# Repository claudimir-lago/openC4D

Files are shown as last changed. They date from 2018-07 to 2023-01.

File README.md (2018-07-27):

# openC4D
#### _A Capacitively Coupled Contactless Conductivity Detector (C4D) for Capillary Electrophoresis._

To the best of our knowledge, this is still the smallest Capacitively Coupled Contactless Conductivity Detector (C4D) … and it’s open!

Our first C4D was introduced in 1998 [1], and after trials and errors, we published an improved version in 2009 [2]. Here, the continuously improved version is available.

What is here?

•	The plans to build __the printed circuit boards for the detector__ itself. It must be powered, and the signal is available as a digital output in a serial format.

•	__The microcontroller board.__ Although the detector module can be used in a dedicated instrument, this board allows one to control up to four C4Ds through a USB port.

•	__The firmware.__ An Arduino firmware to be used in the microcontroller board.

•	__The frontend.__ A Java frontend to be used to get electropherograms.

We have some papers if you wish to learn more about our CE-C4D [1-8].

1.	da Silva, J.A.F. and C.L. do Lago, An oscillometric detector for capillary electrophoresis. Analytical Chemistry, 1998. 70(20): p. 4339-4343.
2.	Francisco, K.J.M. and C.L. do Lago, A compact and high-resolution version of a capacitively coupled contactless conductivity detector. Electrophoresis, 2009. 30(19): p. 3458-3464.
3.	Brito-Neto, J.G.A., et al., Understanding capacitively coupled contactless conductivity detection in capillary and microchip electrophoresis. Part 1. Fundamentals. Electroanalysis, 2005. 17(13): p. 1198-1206.
4.	Brito-Neto, J.G.A., et al., Understanding capacitively coupled contactless conductivity detection in capillary and microchip electrophoresis. Part 2. Peak shape, stray capacitance, noise, and actual electronics. Electroanalysis, 2005. 17(13): p. 1207-1214.
5.	Francisco, K.J.M. and C.L. do Lago, A capillary electrophoresis system with dual capacitively coupled contactless conductivity detection and electrospray ionization tandem mass spectrometry. Electrophoresis, 2016. 37(12): p. 1718-1724.
6.	Francisco, K.J.M. and C.L. do Lago, Improving thermal control of capillary electrophoresis with mass spectrometry and capacitively coupled contactless conductivity detection by using 3D printed cartridges. Talanta, 2018. 185: p. 37-41.
7.	Saito, R.M., et al., Ionic mobility of the solvated proton and acid-base titration in a four-compartment capillary electrophoresis system. Analytical Methods, 2010. 2(2): p. 164-170.
8.	da Silva, J.A.F., N. Guzman, and C.L. do Lago, Contactless conductivity detection for capillary electrophoresis - Hardware improvements and optimization of the input-signal amplitude and frequency. Journal of Chromatography A, 2002. 942(1-2): p. 249-258.

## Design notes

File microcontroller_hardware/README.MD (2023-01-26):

This microcontroller board allows you to connect up to four openC4Ds to an USB port. Then, you can use the [frontend](https://github.com/claudimir-lago/openC4D/tree/master/frontend) for data acquisition or send [Serine commands](https://github.com/claudimir-lago/openC4D/blob/master/firmware/Manual_openC4D_3.pdf) using a [terminal program](https://sites.google.com/site/terminalbpp/).

The original version of the board is based on a [Teensy 2.0 board](https://www.pjrc.com/store/teensy.html), and the one-layer PCB was created in [Eagle](https://www.autodesk.com/products/eagle/free-download). Unfortunately, Teensy 2.0 was discontinued. So, for new projects, consider the Arduino-shield version.

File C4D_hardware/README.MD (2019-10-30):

# Building an openC4D
### _The basics about what you have here_

The openC4D is composed of four printed circuit boards (PCBs): the oscillator, the rectifier, and two shielding boards. Inside the folders Oscillator and Rectifier, you will find the schematics and PCB images. The original files were made in [DipTrace](https://diptrace.com/download/download-diptrace/).

Whether you wish a fast track, go straight to Gerber and send the files to some place for the production of a panel with PCBs for one complete openC4D.

### _An warning about the previous version of the printed circuit boards_

The previous version of the PCBs was made available as a panel with the boards for three detectors. There was, however, a small but important failure in the tracks. Unfortunately, two tracks were merged in some point during the production, and now they must be fixed. Figure 1 shows that board and the two small cuts that must be done in the oscillator board. You can use a sharp (and hard) device to cut the merged tracks… and that’s all.

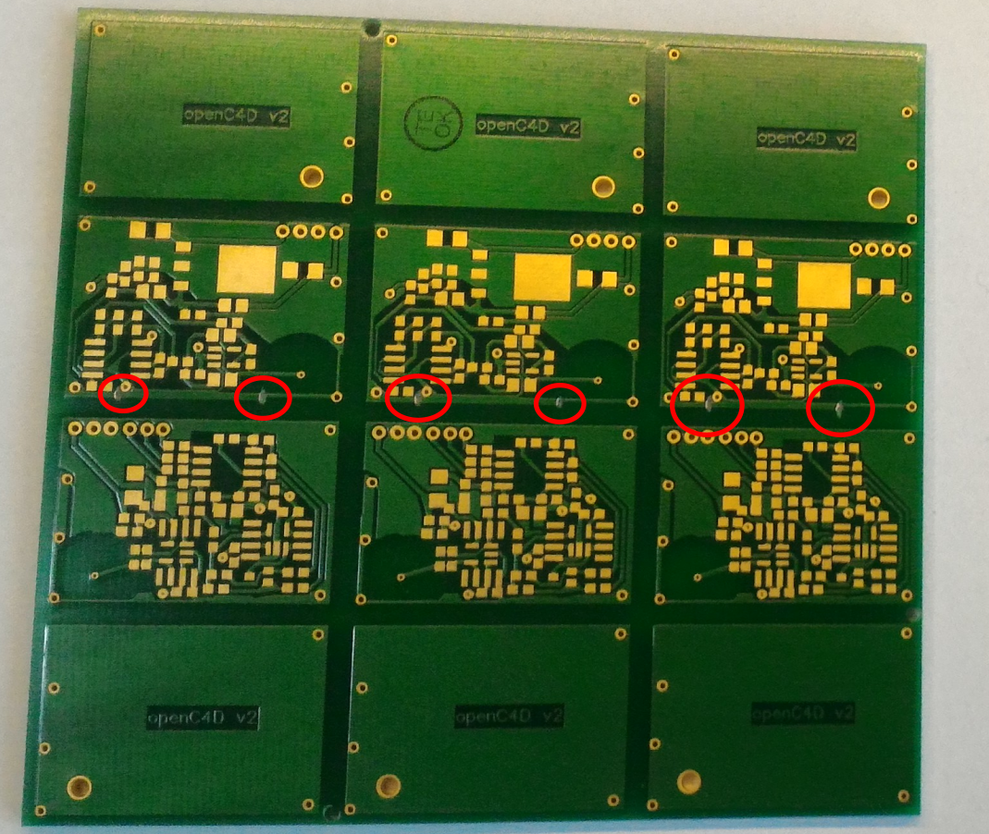
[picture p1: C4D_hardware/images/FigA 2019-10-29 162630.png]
Figure A

#### _Figure 1._ The red circles show where to cut the tracks. Don’t worry, because there are redundant tracks keeping the right connections between the parts.

### _A step-by-step building process (with tips and tricks)_

Although the present files are for one detector, this tutorial is based on the previous paneled version, but don’t worry. As shown in Figure 2, after marking the borders and cutting off the boards, you will have essentially the same boards that you need to build the openC4D.

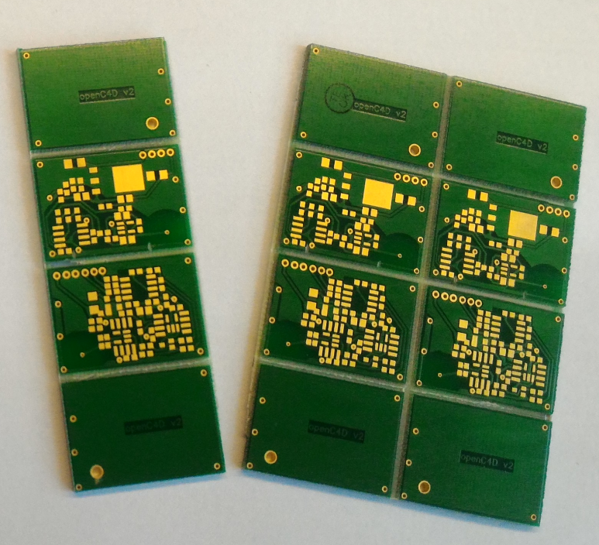
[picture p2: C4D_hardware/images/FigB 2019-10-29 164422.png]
Figure B

#### _Figure 2._ We used a CNC machine to make the grooves between all PCBs, but you can use any other method to cut FR04 PCBs. After that, the PCBs are separated, and the borders are sanded accordingly.

The four PCBs will be assembled as a “sandwich”, but we need the stuffing for the sandwich: two insulant layers and the ground plane, as shown in Figure 3. These layers will be put between the oscillator and rectifier PCBs and will determine the gap between the electrodes, which essentially determine the detection length.

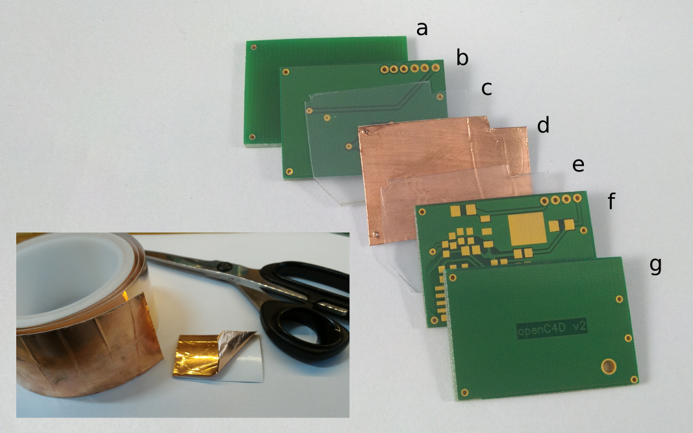
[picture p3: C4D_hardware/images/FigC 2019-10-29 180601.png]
Figure C

#### _Figure 3._ The set of seven layers of an openC4D: shield PCBs (a and g), rectifier PCB (b), insulating layers (c and e), copper ground plane (d), and oscillator PCB (f). The copper layer was prepared from a copper foil tape (shown in the inset). After cutting, the copper layer is pulled off and stick to one of the insulating layers.

Different materials can be used for the insulating and ground plane layers.

In Figure 3, the material used to make the insulating layers was a 0.25-mm PVC foil – actually, it was previously part of the cover of an old notebook. Obviously, the companies create the cover to cover a document and not necessarily to be used as an insulating layer. We’ve learned that some black covers are not appropriate, because they become somewhat conductive at high frequency (must likely because of the black filler or pigment).

The ground plane can be made of aluminum, copper, brass, or other conductive material. Copper foil tape is convenient, because it is thin and self-adhesive. Thicker foils will increase the coupling of the ground plane with the solution inside the capillary, and it is not good. At the same time, the thin foil of copper can be stick to one of the insulation layer, which ease the alignment of the different layers.

Be careful in making the holes through which the capillary will pass. For instance, a small barb in the copper layer could get into electrical contact with one of the electrodes from either the oscillator or the rectifier PCBs. Make sure, thus, that the holes are clear of barbs to prevent short circuits. 

The PCBs were prepared for SMD components, but there are a two options for the integrated circuits (ICs) U1 and U2 in the rectifier PCB: 5-pin SOT-23 and 8-pin SOIC. Figure 4 shows PCBs populated with these two kinds of components. SOT-23 has a smaller footprint, but SOIC is more popular. The idea was to make a board that could accept these two different versions of operational amplifiers available in the market. There is, however, a very important trick here: **the 5-pin SOT-23 must be soldered upside-down!!!** This was the price to make the board flexible and simple at the same time. Whether you can get the 8-pin SOIC version, buy it because it is safer and usually cheaper solution.

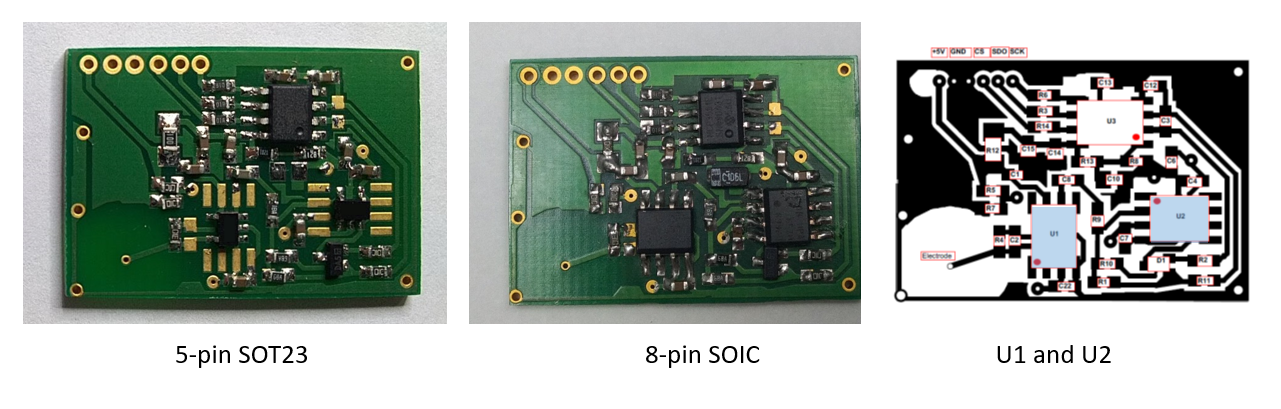
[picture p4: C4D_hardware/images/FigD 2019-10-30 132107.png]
Figure D

#### _Figure 4._ The rectifier PCB populated with the two versions of U1 and U2. It sounds strange, but the 5-pin SOT-23 ICs must be positioned upside-down before soldering.

Although a connector can be soldered at the border of the PCB, we’ve used to solder the cable to the boards, because the final setup is more robust and compact. In this case, make sure that the solder joint has a low profile as shown in Figure 5 in order to prevent that it touches the other PCB. You should try to make a proper [solder joint]( https://learn.adafruit.com/adafruit-guide-excellent-soldering/tools) and cut off the excess after that.

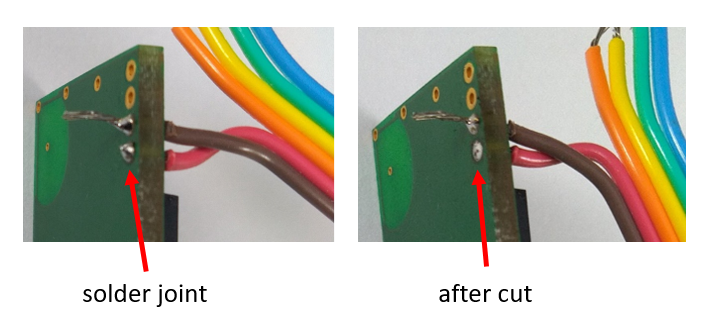
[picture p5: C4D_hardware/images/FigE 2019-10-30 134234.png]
Figure E

#### _Figure 5._ Pictures of a solder joint before and after the cutoff.

Before finishing, it is a good idea to check the voltages and waveforms at the test points.

The wave at the output of U1.2 (Figure 6) should be a square wave swinging between 0 and 5 V at a frequency around 1 MHz. A triangular wave is expected at the output of U1.1 and its amplitude should be about 4 V. At the output of U2 a sine wave is expected with amplitude also of 4 V. Although the original values of the resistors and capacitors were calculated according to these directives, the experimental result is not always the same. Sometimes only minor nonconformities are detected. However, sometimes the result is quite different. Unfortunately, there is no other way but changing resistors and capacitors. It is possible to calculated the values, but it is important having in mind some hints:

•	The higher either R2 or C1, the lower the oscillation frequency;

•	R1/R3 determines the amplitude of the triangular wave;

•	U2.1 with R4, R5, R6, C6, and C7 are a [multiple feedback low-pass filter](http://sim.okawa-denshi.jp/en/OPtazyuLowkeisan.htm) that should cut off the harmonics of the triangular wave and give a small gain to the fundamental frequency.

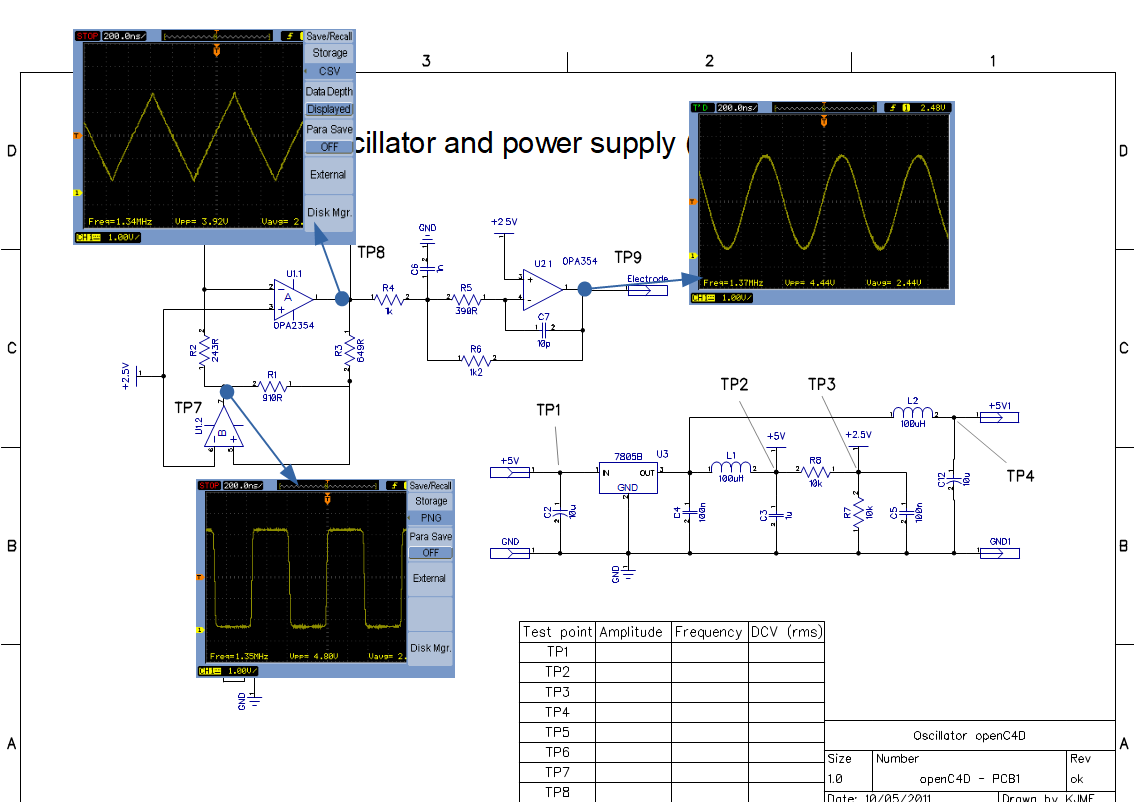
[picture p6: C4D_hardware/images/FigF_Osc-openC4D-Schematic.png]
Figure F

#### _Figure 6._ Waveforms at the most important test points in the oscillator board.

The waveform at the output of the transimpedance amplifier (U1.1 in Figure 7) should be a sine wave with the same frequency of the signal at the output of the oscillator. However, such a signal is detected only if the silica capillary is inserted in the detector. Without the capillary, only a flat line is observed. Figure 7 shows the results with an empty capillary. If the capillary is filled with a conductive solution, the amplitude should be higher.

The waveform at the output of U2.1 is not exactly a sine wave, because of the diodes, but it should respond to the output of the transimpedance amplifier. At TP9 and TP10, the negative and positive half waves, respectively, should be detected. Similar to all other alternated signals showed in these figures, there is a +2.5-V offset.

Finally, after the RC filters (input of the analog-to-digital converter), only flat lines should be detected. 

If everything is OK, it’s time to finish the assembly (Figure 8).

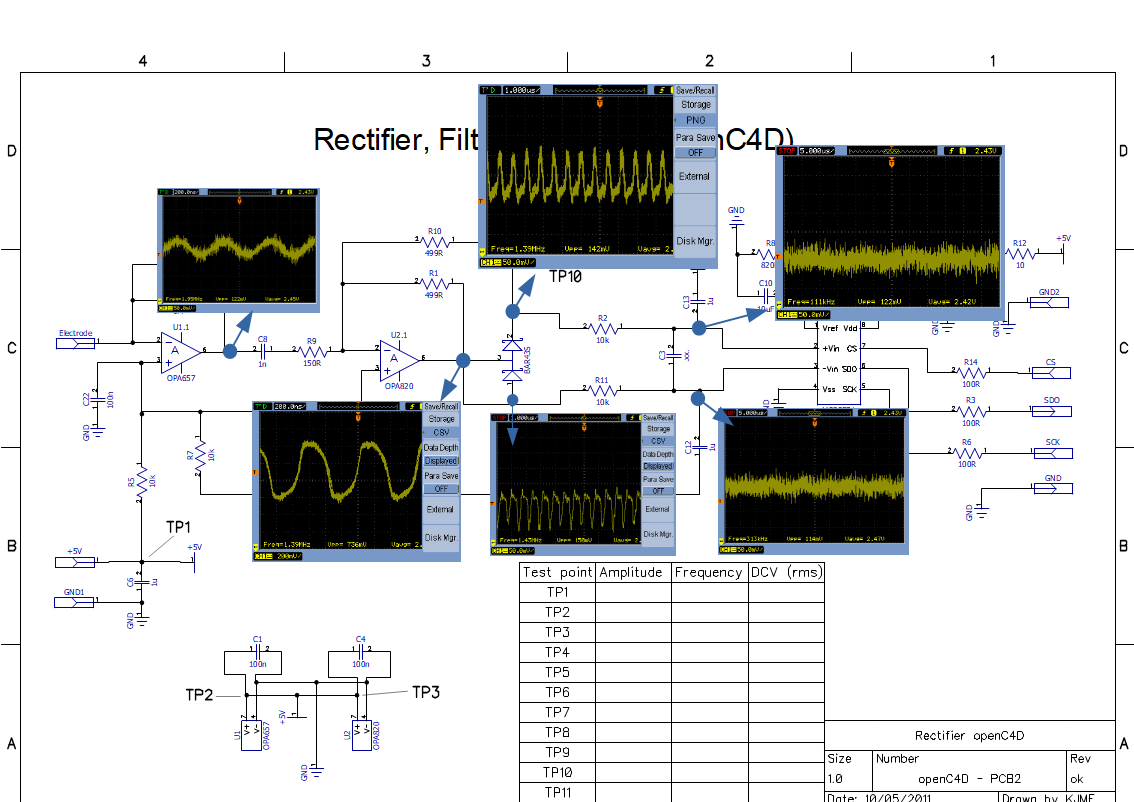
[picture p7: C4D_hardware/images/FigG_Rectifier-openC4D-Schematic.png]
Figure G

#### _Figure 7._ Waveforms at the most important test points in the rectifier board.

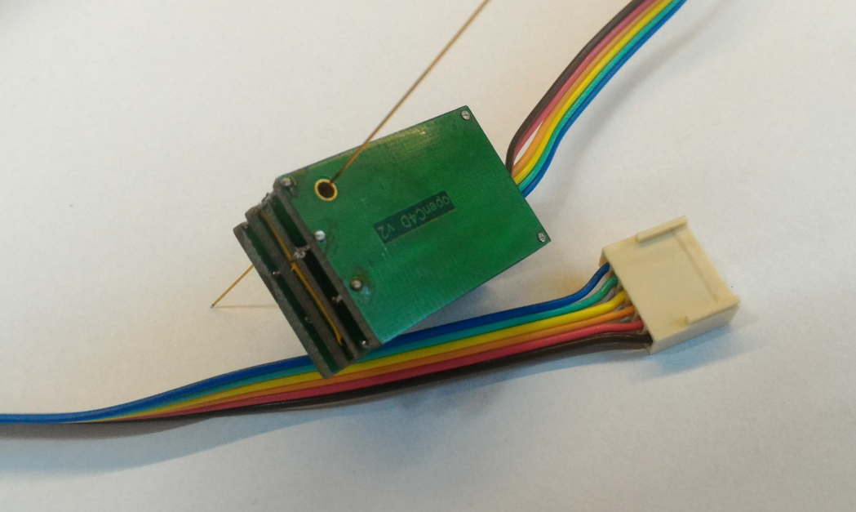
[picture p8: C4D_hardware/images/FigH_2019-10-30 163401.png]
Figure H

#### _Figure 8._ An almost finished openC4D. Please note that the detector has not yet been filled with silicone. We will return to this stage in the future.

#### _Thanks to Eric T. da Costa and Kelliton J. M. Francisco_

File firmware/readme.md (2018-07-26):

The firmware was developed on [Arduino](https://www.arduino.cc/) platform using [Serine Protocol](https://github.com/claudimir-lago/Serine-Protocol). The available version is based on a Teensy 2.0 board. We hope to deploy versions for an Arduino board soon.

The [manual](https://github.com/claudimir-lago/openC4D/blob/master/firmware/Manual_openC4D_3.pdf) allows you developing a frontend in any language. Actually, you can use just a terminal program to send ASCII messages and get C4D data.

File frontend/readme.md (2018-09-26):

The frontend is a [Java](https://en.wikipedia.org/wiki/Java_(programming_language)) program. You run, check in which serial port the C4D is available, connect with it, and start using.

__openC4Ddist.zip__ contains all you need to run the frontend.

__openC4D__ is a [NetBeans](https://netbeans.org/downloads/) project with the source code.

The frontend uses jSSC (Java Simple Serial Connector), JFreeChart, jLAIA, and SerineProtocol, which are LGPL libraries.

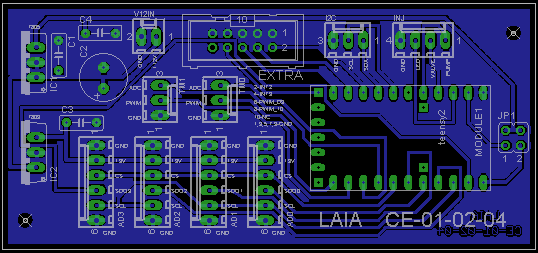
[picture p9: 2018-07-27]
microcontroller_hardware/Teensy_2.0/images/CE-01-02-04_v01_brd.png

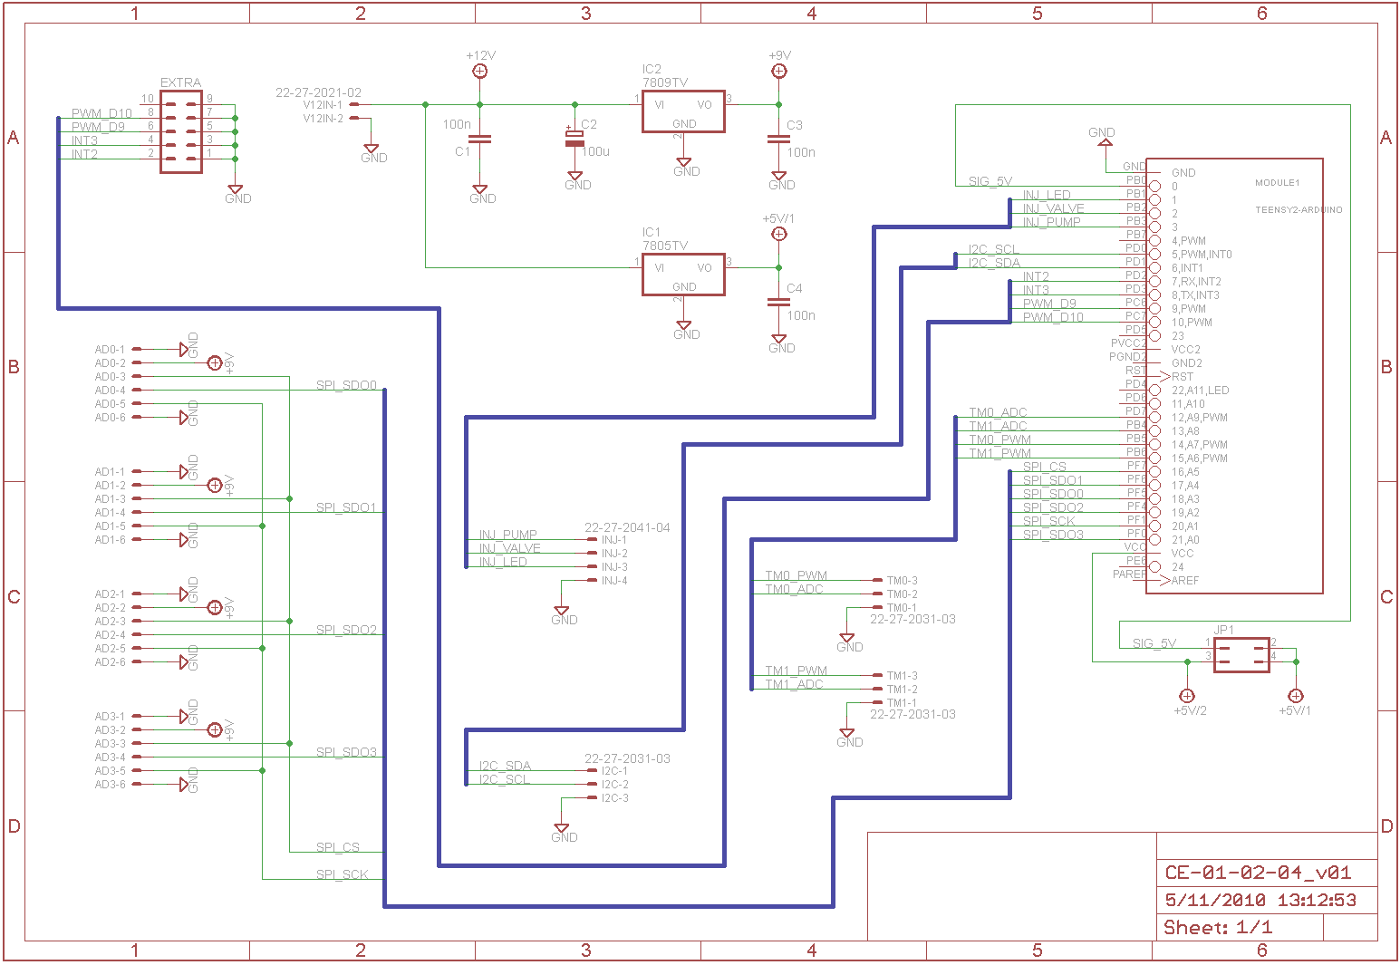
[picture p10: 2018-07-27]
microcontroller_hardware/Teensy_2.0/images/CE-01-02-04_v01_sch.png

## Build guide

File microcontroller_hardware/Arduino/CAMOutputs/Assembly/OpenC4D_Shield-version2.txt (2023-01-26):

Partlist exported from D:/pop/posdoc/projetos/C4D/OpenC4D_Shield_Version2/OpenC4D_Shield-version2.sch at 28/10/2021 13:18

Qty Value                      Device                     Package       Parts              Description                          SPICEMODEL SPICEPREFIX
4                              22-27-2061-06              6410-06       AD0, AD1, AD2, AD3 CONNECTOR                                                  
4                              R0204/7                    0204/7        R1, R2, R3, R4     RESISTOR, European symbol            NONE       R          
2   100n                       C-EU050-025X075            C050-025X075  C1, C3             CAPACITOR, European symbol                                 
1   100u                       CPOL-EUE3.5-8              E3,5-8        C2                 POLARIZED CAPACITOR, European symbol                       
3   22-27-2031-03              22-27-2031-03              6410-03       I2C, TM0, TM1      CONNECTOR                                                  
1   7809TV                     7812TV                     TO220V        IC2                Positive VOLTAGE REGULATOR                                 
1   ARDUINO_UNO_R3_SHIELDBASIC ARDUINO_UNO_R3_SHIELDBASIC UNO_R3_SHIELD B1                 Arduino R3 Shield Footprint                     X          
1   ext0                       ML10                       ML10          EXT-0              HARTING                                                    
1   ext1                       ML10                       ML10          EXT-1              HARTING

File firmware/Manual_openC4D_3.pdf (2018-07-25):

# openC⁴D

# Serine Protocol Communication Manual

# Version 3

by

## Claudimir Lucio do Lago Department of Fundamental Chemistry University of São Paulo Brazil

## April 2018

17/4/2018 – 12:45:33 | 1

# Contents

## Introduction

The hardware was conceived using a Teensy 2.0 allowing up to four capacitively coupled conductivity detectors (C⁴Ds). The detectors are numbered from 0 to 3. The communication with the openC⁴D is allowed through a serial port over USB.
The command Connect allows establishing a connection with the detector. When connected, a continuous mode of transmission of the ADC data is possible. In this case, the user does not need to ask for each new ADC value, because they are sent continuously.
The transmission mode is established by the Set command. This command also allows choosing the format of the data sending back to the user. It is possible configure the answer as a formatted data (according Serine Protocol), or a simple ASCII line (one-way Serine), which allows data acquisition without a Serine front end.
According to the Serine Protocol, the ID may be changed by the command “Ix”. In this case, the new ID must be used instead of the default ID ‘d’. For sake of simplicity, in this manual, the other virtual device exchanging messages is always ‘m’. However, in real communication this character should be replaced by the valid ID of the virtual device that is communicating with the detector.
The “\0” at the end of each message is just to remember that an additional position with a null character (ASCII code 0) at the end of the array is needed for most of the program languages (such as C, C++, Java, etc.). However, it is not part of the Serine Protocol.

## Commands

## Identification

This command allows get the ID of the virtual device as well as to change it.

Command string:

0 | 1 | 2 | 3 | 4 | 5 | 6 | 7 | 8 | 9 | 10 | 11 | 12 | 13 | 14 | 15 | 16 | 17 | 18 | 19 | 20 | 21 | 22 | 23 | 24 | 25 | 26 | 27 | 28 | 29 | 30 | 31 | 32
d | m | I | ; | \0

Return string:

0 | 1 | 2 | 3 | 4
m | d | i | y | s | … | s | ; | \0

y – ‘t’ means that the following string (s…s) is a temporary identification; ‘P’ means that the following string (s…s) is a proprietary identification; ‘S’ means that the following string (s…s) is a valid ID provided by Serine Identification Service (SIS). Other character may be used by other public providers of identification service.

Change – command string:

0 | 1 | 2 | 3 | 4 | 5
d | m | I | x | y | s | … | s | ; | \0

y – is the new ID to be adopted by the detector if the following string (s…s) is equal to its identification string. If the ID is changed, all the other messages exchanged with this device must use it instead of the default ID ‘d’.

Examples:

Sender | This device | Comment
dmI; | mdit_just_a_test; | The device has a temporary identification “t_just_a_test”
dmI; | mdiSdL012042; | The device is the SIS virtual device dL01, version 2, serial number 042.
dmIxwSdL012042; | | The device identified with “SdL012042” has now the ID w instead of d;

## Connect

This command allows establishing a connection and warning the detector that the listener is ready to get data continuously.

Command string:

0 | 1 | 2 | 3 | 4 | 5 | 6 | 7 | 8 | 9 | 10 | 11 | 12 | 13 | 14 | 15 | 16 | 17 | 18 | 19 | 20 | 21 | 22 | 23 | 24 | 25 | 26 | 27 | 28 | 29 | 30 | 31 | 32
d | m | X | y | ; | \0

Return string:

0 | 1 | 2 | 3 | 4 | 5 | 6 | 7 | 8 | 9 | 10 | 11 | 12 | 13 | 14 | 15 | 16 | 17 | 18 | 19 | 20 | 21 | 22 | 23 | 24 | 25 | 26 | 27 | 28 | 29 | 30 | 31 | 32
m | d | x | y | ; | \0

y – 'N' means connection is ON; 'F' means connection is OFF.

Examples:

Sender | This device | Comment
dmXN; | dmxN; | The detector recognized the connection.
dmXF; | dmxF; | The connection was turned off.

## Zero

This command reinitiates the chronometer.

Command string:

0 | 1 | 2 | 3 | 4 | 5 | 6 | 7 | 8 | 9 | 10 | 11 | 12 | 13 | 14 | 15 | 16 | 17 | 18 | 19 | 20 | 21 | 22 | 23 | 24 | 25 | 26 | 27 | 28 | 29 | 30 | 31 | 32
d | x | Z | ; | \0

## Set

This command configures the way the command Get will work. See command Get for more information.

Command string:

0 | 1 | 2 | 3 | 4 | 5 | 6 | 7 | 8 | 9 | 10 | 11 | 12 | 13 | 14 | 15 | 16 | 17 | 18 | 19 | 20 | 21 | 22 | 23 | 24 | 25 | 26 | 27 | 28 | 29 | 30 | 31 | 32
d | m | S | y | t | a0 | a1 | a2 | a3 | ; | \0

Position:
y – ‘f’ set the output to send back Serine-formatted data. Any other character indicates to operate in the one-way Serine, and this character will be used as a separator.

The only exceptions are ‘t’ standing for tab and ‘s’ standing for space. Any valid Serine character can also be used.
t – '1' indicates that a time stamp should be included in the ASCII string.
ax – '1' indicates that the data from ADC x should be included in the response.

## Get

This command instructs the virtual device to send back the values of the A/D converters. It is possible to put the virtual device in a continuous mode sending each new value obtained from the ADCs, as well as to instruct about the data format.

Command string:

0 | 1 | 2 | 3 | 4 | 5 | 6 | 7 | 8 | 9 | 10 | 11 | 12 | 13 | 14 | 15 | 16 | 17 | 18 | 19 | 20 | 21 | 22 | 23 | 24 | 25 | 26 | 27 | 28 | 29 | 30 | 31 | 32
d | m | G | y | ; | \0

y – 'r' sets the continuous mode; 'h' halts the continuous mode; ‘w’ waits for the external start; ‘t’ waits for the external start and stop; ‘S’ requests the status. Any other option will result in just one instantaneous get.

Return string for option 'f' (Serine formatted):

0 | 1 | 2 | 3 | 4 | 5 | 6 | 7 | 8 | 9 | 10 | 11 | 12 | 13 | 14 | 15 | 16 | 17 | 18 | 19 | 20 | 21 | 22 | 23 | 24 | 25 | 26 | 27 | 28 | 29 | 30 | 31 | 32
m | d | g | y | t | t | t | t | t | t | t | aw aw aw aw aw aw aw | | | | | | | ax | ax | ax | ax | ax | ax | ax | ; | \0

y – ‘A’ means the first block of detector (ADCs 0 and 1); ‘B’ means the second block of detector (ADCs 2 and 3).
t – time in milliseconds (seven digits).
aw a az – readings (from 0 to 4,194,304) of the ADCs 0 and 1, for y = ‘A’, or 2 and 3, for y = ‘B’.

Return string for status request (for Serine formatted option only):

0 | 1 | 2 | 3 | 4 | 5 | 6 | 7 | 8 | 9 | 10 | 11 | 12 | 13 | 14 | 15 | 16 | 17 | 18 | 19 | 20 | 21 | 22 | 23 | 24 | 25 | 26 | 27 | 28 | 29 | 30 | 31 | 32
m | d | g | S | x | y | z | ; | \0

x – ‘T’ means that the detector is in the continuous mode.
y – ‘T’ means that the detector is waiting for an external start pulse. z – ‘T’ means that the detector is waiting for an external stop pulse.

Return string for one-way Serine in command Set:

0 | 1 | 2 | 3 | 4 | 5 | 6 | 7 | 8 | 9 | 10 | 11 | 12 | 13 | 14 | 15
ax | ax | ax | ax | ax | ax | ax | s | ay | ay | ay | ay | ay | ay | ay | s | … az | az | az | az | az | az | az | lf | \0

ax to az – time and/or ADC readings according to the command Set. s – separator according command to the command Set.
lf – ASCII line feed.

Examples:

Master | This device | Comment

dmSs10011;dmZ;dmGr; 0000025 2153341 2271077

| 0000108 2153334 2271096 0000174 2153356 2271103 0000256 2153305 2271093 0000323 2153342 2271082 0000391 2153334 2271080 0000473 2153366 2271080 0000541 2153307 2271102 0000609 2153354 2271090 0000691 2153345 2271086 …

The detector was configure to answer as one-way Serine,
with spaces to separate
columns, the first column is the time in milliseconds
followed by the readings of detectors 2 and 3. The
chronometer is initiated, and a continuous reading mode is initiated.
dmGh; | The data transmission is stopped.
Master | This device | Comment
dmSf10011;dmZ;dmGr; | mdgB0000063215338222 71005;mdgB00001372153 3682270994;mdgB000020 921533672270994;mdgB0 00028521534102270967; mdgB0000356215338222 71006;mdgB00004302153 3462270993;mdgB000050 221533712270980;mdgB0 00057621533752270974; mdgB0000651215336322 70980; …

The readings of the detectors 2 and 3 (block B) will be
returned in Serine-formatted strings. The chronometer is initiated, and a continuous reading mode is initiated.
dmGh; | The data transmission is stopped.

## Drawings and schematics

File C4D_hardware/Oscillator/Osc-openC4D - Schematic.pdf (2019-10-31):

# Oscillator and power supply (openC4D)

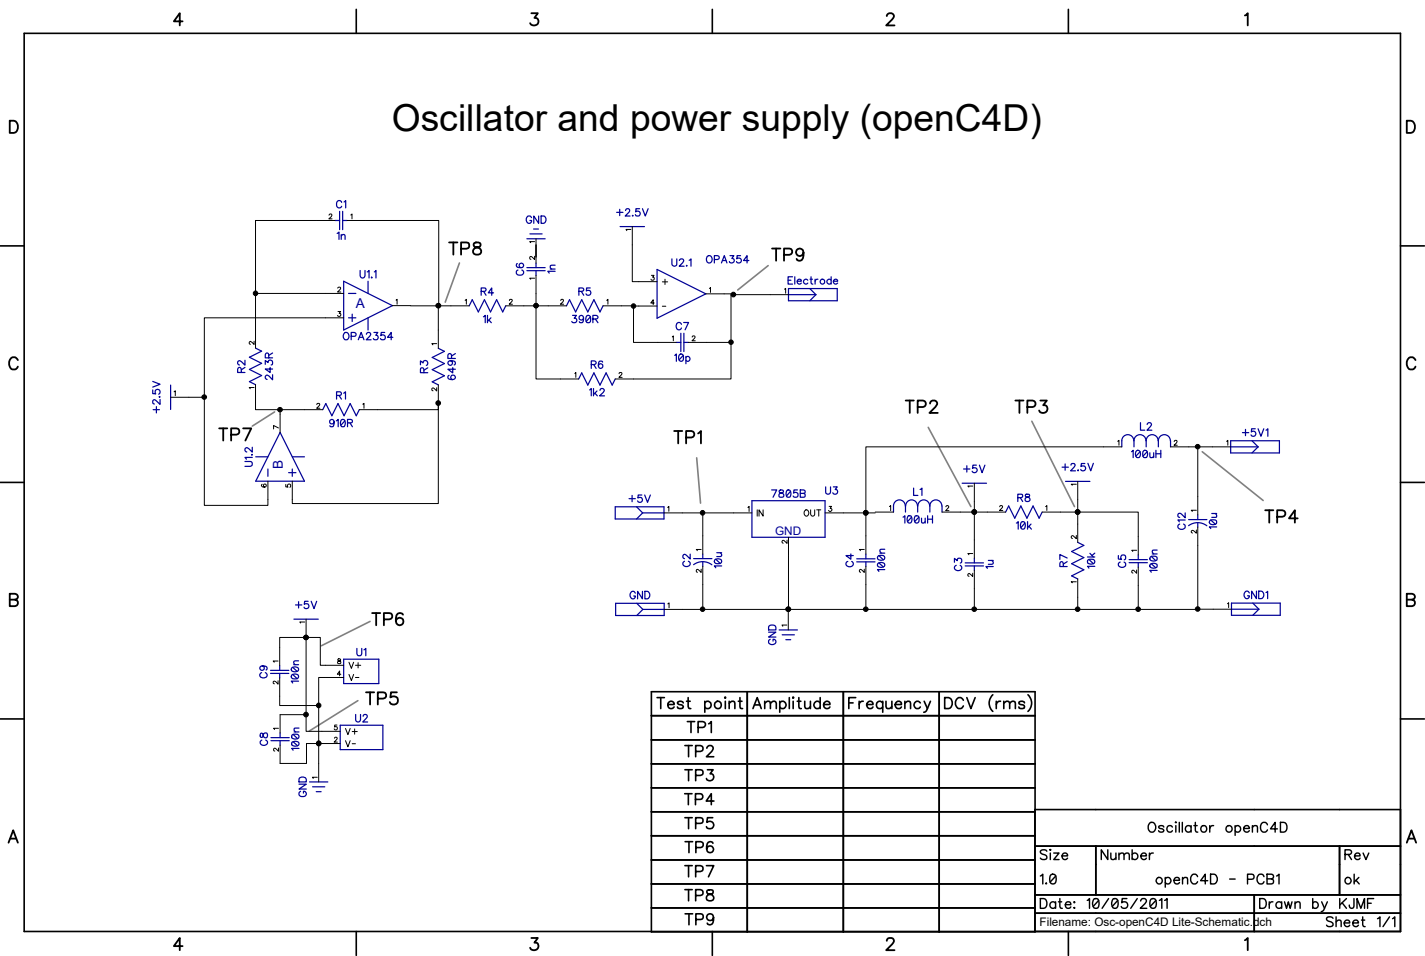
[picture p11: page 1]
GND

Filename: Osc-openC4D Lite-Schematic.dch

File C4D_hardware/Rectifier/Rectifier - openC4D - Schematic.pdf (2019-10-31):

# Rectifier, Filter, and ADC (openC4D)

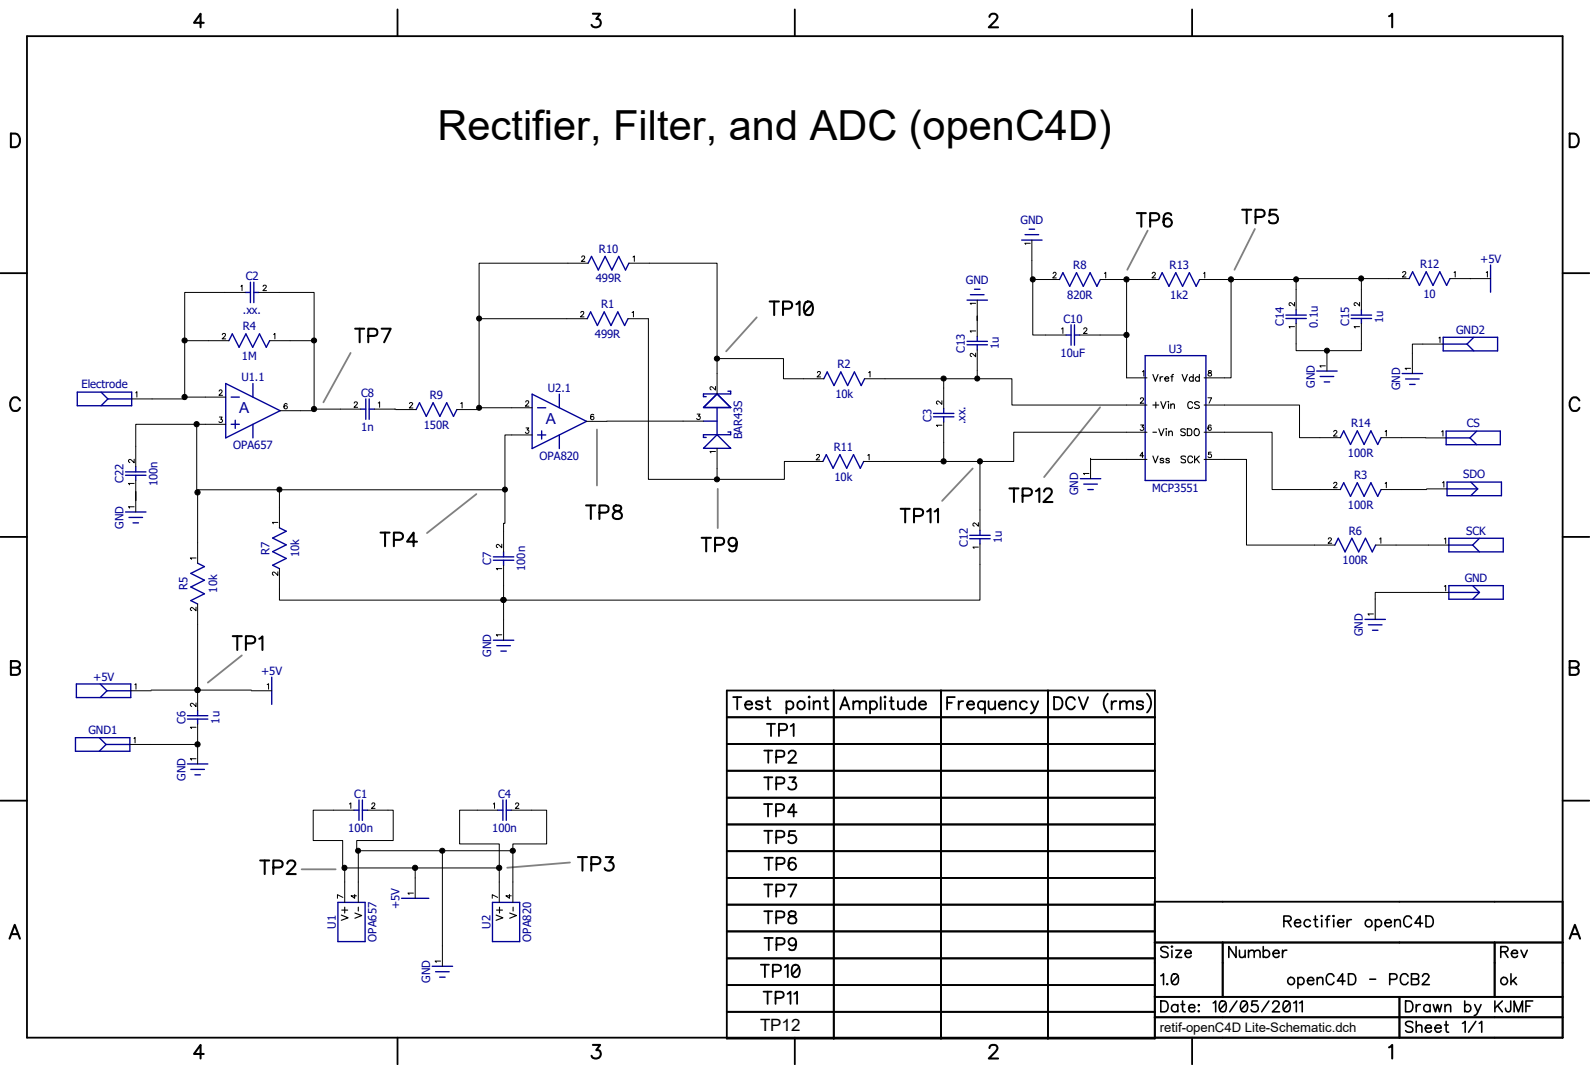
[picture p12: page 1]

retif-openC4D Lite-Schematic.dch

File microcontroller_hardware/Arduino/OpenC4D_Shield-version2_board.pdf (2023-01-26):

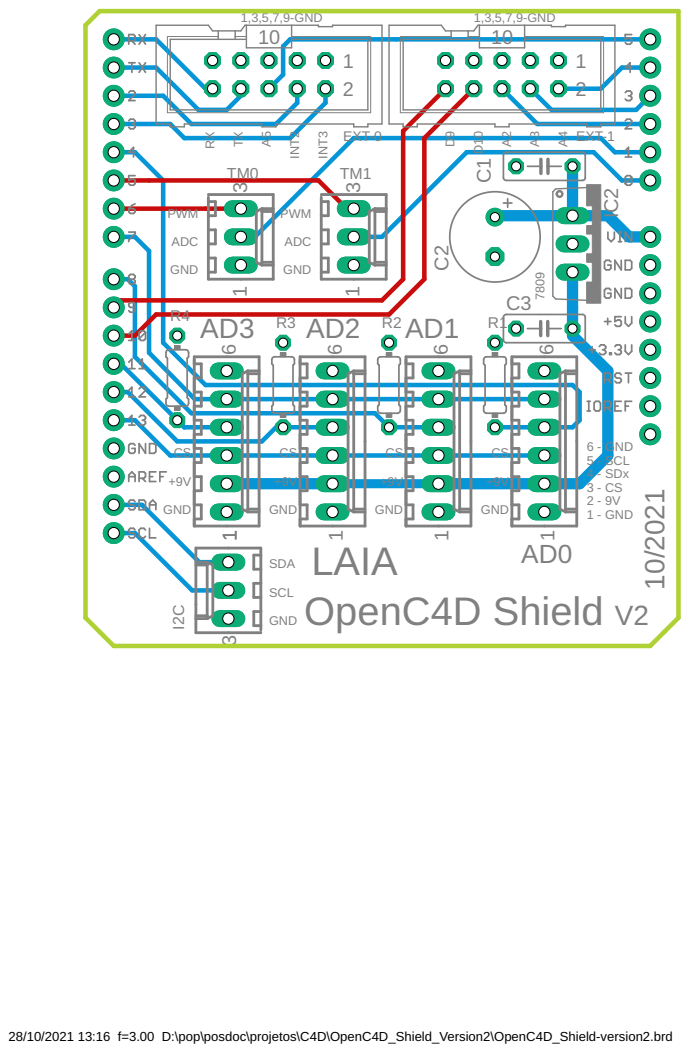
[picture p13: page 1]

28/10/2021 13:16 f=3.00 D:\pop\posdoc\projetos\C4D\OpenC4D_Shield_Version2\OpenC4D_Shield-version2.brd

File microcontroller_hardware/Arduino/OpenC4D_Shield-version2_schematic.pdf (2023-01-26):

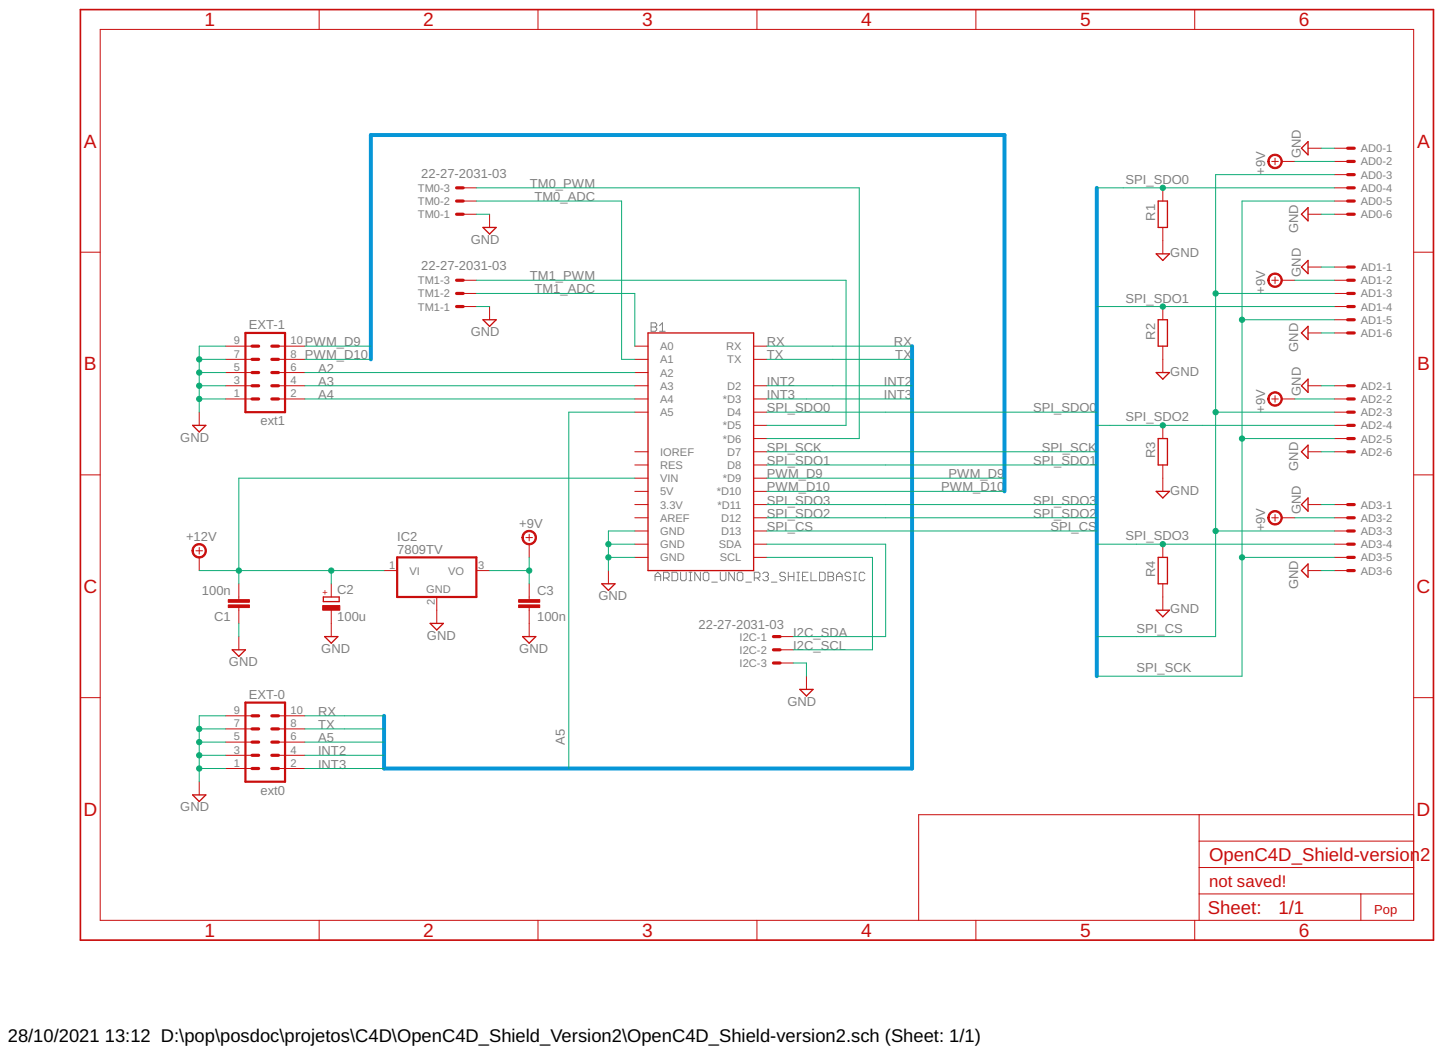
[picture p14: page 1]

GND GND GND GND GND GND GND

INT2 | INT2
INT3 | INT3

SPI_SDO2 | SPI_SDO2
SPI_CS | SPI_CS

28/10/2021 13:12 D:\pop\posdoc\projetos\C4D\OpenC4D_Shield_Version2\OpenC4D_Shield-version2.sch (Sheet: 1/1)

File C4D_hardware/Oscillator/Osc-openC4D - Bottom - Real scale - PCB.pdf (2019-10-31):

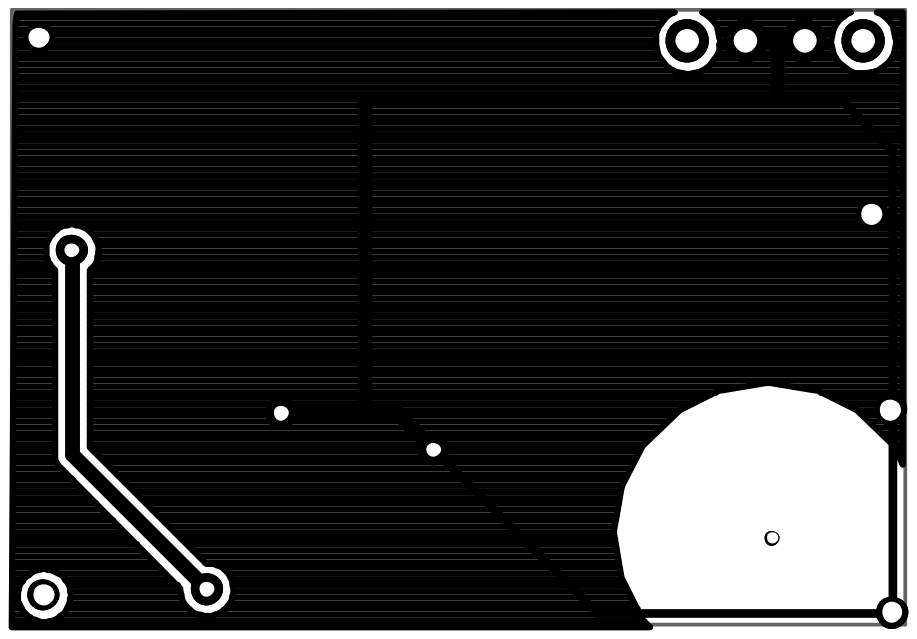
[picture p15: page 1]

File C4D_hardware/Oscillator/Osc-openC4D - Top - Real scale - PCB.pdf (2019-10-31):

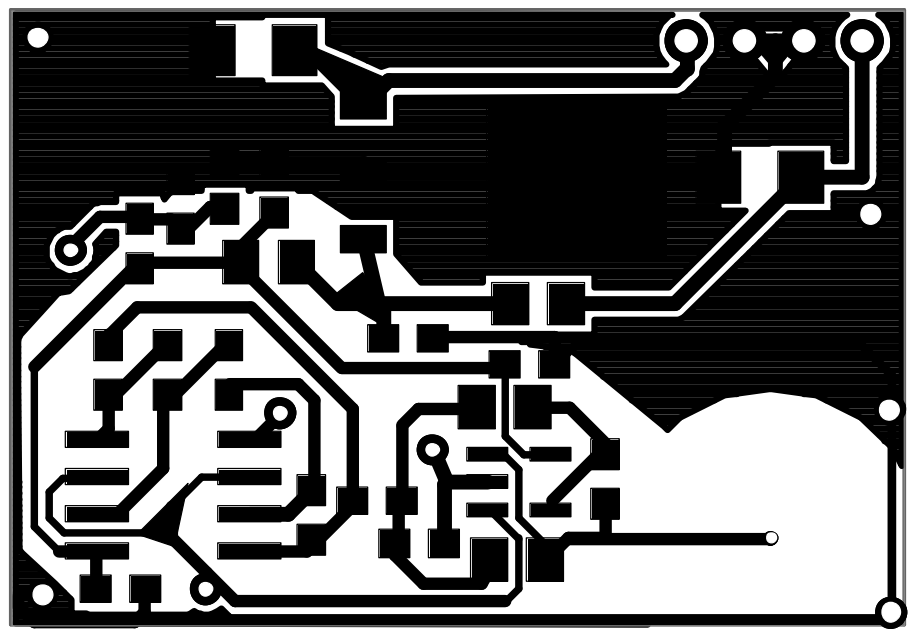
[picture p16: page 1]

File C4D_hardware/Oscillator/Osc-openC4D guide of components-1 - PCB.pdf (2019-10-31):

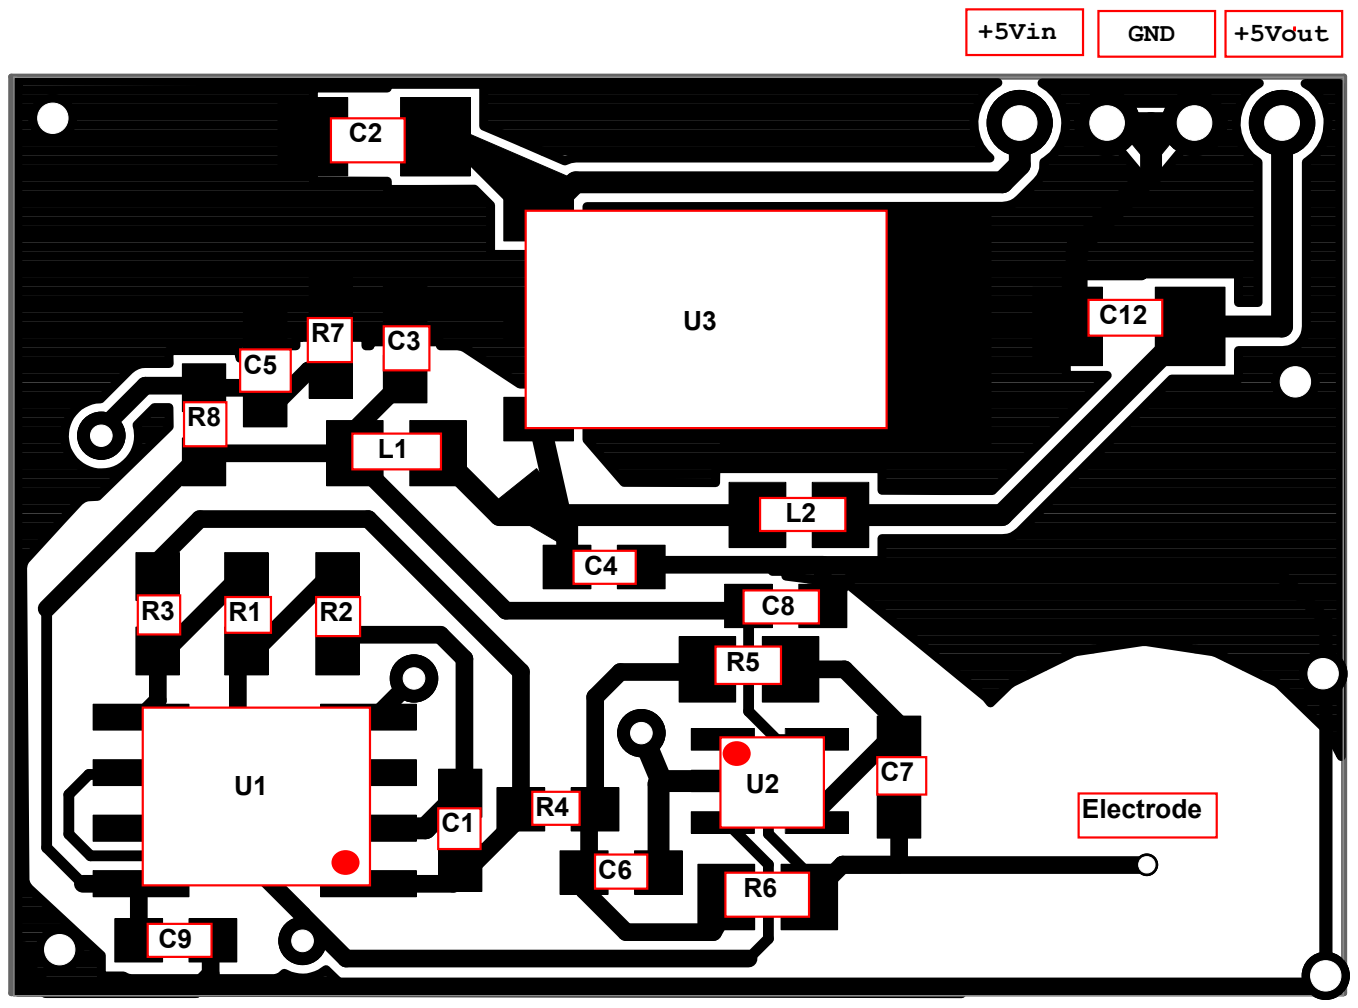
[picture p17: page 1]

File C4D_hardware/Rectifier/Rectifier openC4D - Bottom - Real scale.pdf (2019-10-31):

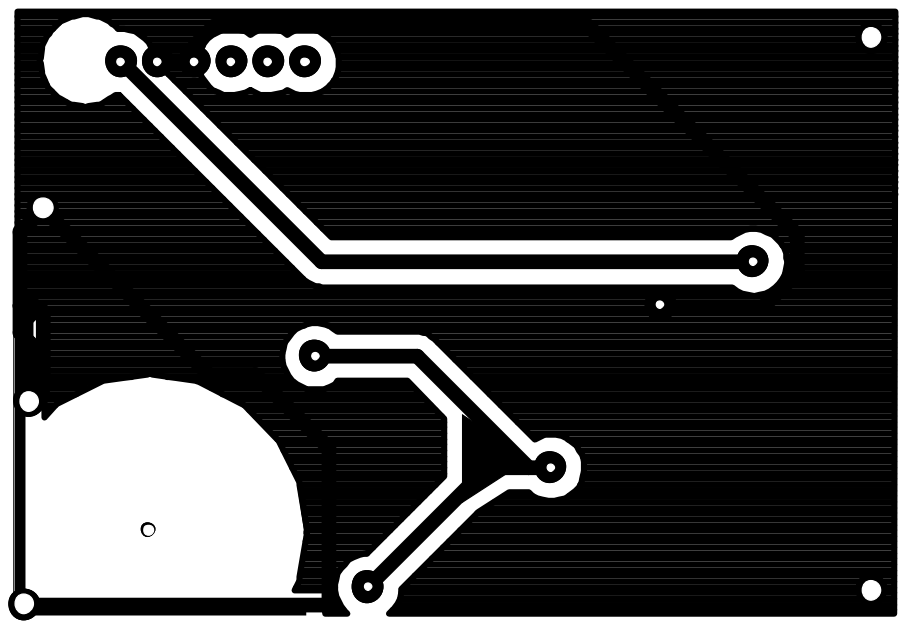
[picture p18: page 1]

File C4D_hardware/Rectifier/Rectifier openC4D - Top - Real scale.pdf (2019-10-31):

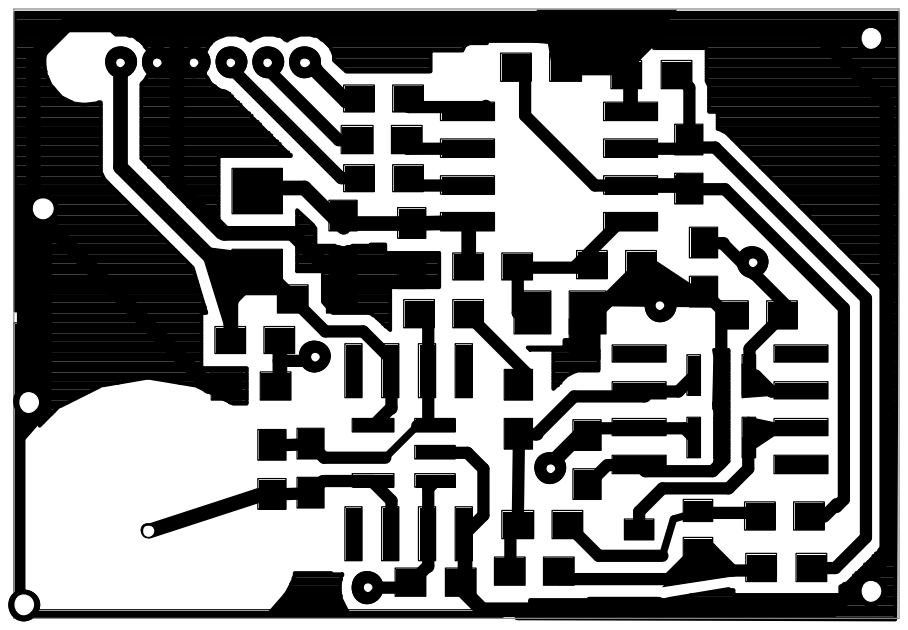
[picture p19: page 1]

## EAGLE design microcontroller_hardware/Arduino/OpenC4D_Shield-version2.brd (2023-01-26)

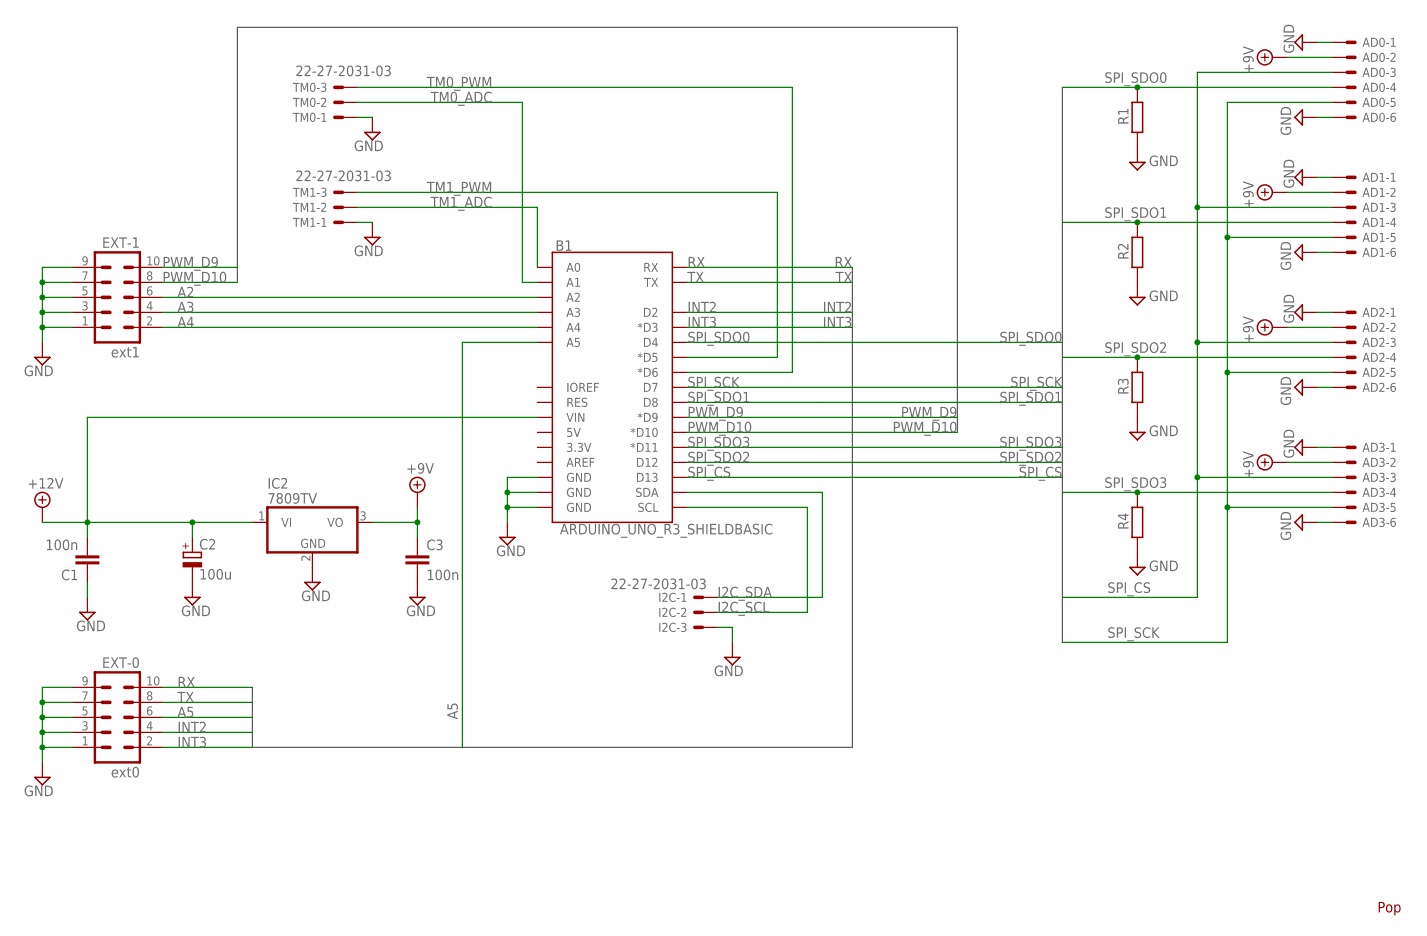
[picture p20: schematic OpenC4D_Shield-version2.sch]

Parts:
AD0, AD1, AD2, AD3: 22-27-2061-06; 6410-06
B1: ARDUINO_UNO_R3_SHIELDBASIC; UNO_R3_SHIELD
C1, C3: 100n; C050-025X075
C2: 100u; E3,5-8
EXT-0: ext0; ML10
EXT-1: ext1; ML10
I2C: 22-27-2031-03; 6410-03
IC2: 7809TV; TO220V
R1, R2, R3, R4: R0204/7; 0204/7
TM0, TM1: 22-27-2031-03; 6410-03

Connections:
+9V: AD0.2, AD1.2, AD2.2, AD3.2, C3.1, IC2.3 (VO)
+12V: B1.VIN, C1.2, C2.+, IC2.1 (VI)
A2: B1.A2, EXT-1.6
A3: B1.A3, EXT-1.4
A4: B1.A4, EXT-1.2
A5: B1.A5, EXT-0.6
GND: AD0.1, AD0.6, AD1.1, AD1.6, AD2.1, AD2.6, AD3.1, AD3.6, B1.GND@0 (GND), B1.GND@1 (GND), B1.GND@2 (GND), C1.1, C2.-, C3.2, EXT-0.1, EXT-0.3, EXT-0.5, EXT-0.7, EXT-0.9, EXT-1.1, EXT-1.3, EXT-1.5, EXT-1.7, EXT-1.9, I2C.3, IC2.2 (GND), R1.1, R2.1, R3.1, R4.1, TM0.1, TM1.1
I2C_SCL: B1.SCL, I2C.2
I2C_SDA: B1.SDA, I2C.1
INT2: B1.D2, EXT-0.4
INT3: B1.D3 (*D3), EXT-0.2
PWM_D9: B1.D9 (*D9), EXT-1.10
PWM_D10: B1.D10 (*D10), EXT-1.8
RX: B1.RX, EXT-0.10
SPI_CS: AD0.3, AD1.3, AD2.3, AD3.3, B1.D13
SPI_SCK: AD0.5, AD1.5, AD2.5, AD3.5, B1.D7
SPI_SDO0: AD0.4, B1.D4, R1.2
SPI_SDO1: AD1.4, B1.D8, R2.2
SPI_SDO2: AD2.4, B1.D12, R3.2
SPI_SDO3: AD3.4, B1.D11 (*D11), R4.2
TM0_ADC: B1.A1, TM0.2
TM0_PWM: B1.D6 (*D6), TM0.3
TM1_ADC: B1.A0, TM1.2
TM1_PWM: B1.D5 (*D5), TM1.3
TX: B1.TX, EXT-0.8

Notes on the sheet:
Pop

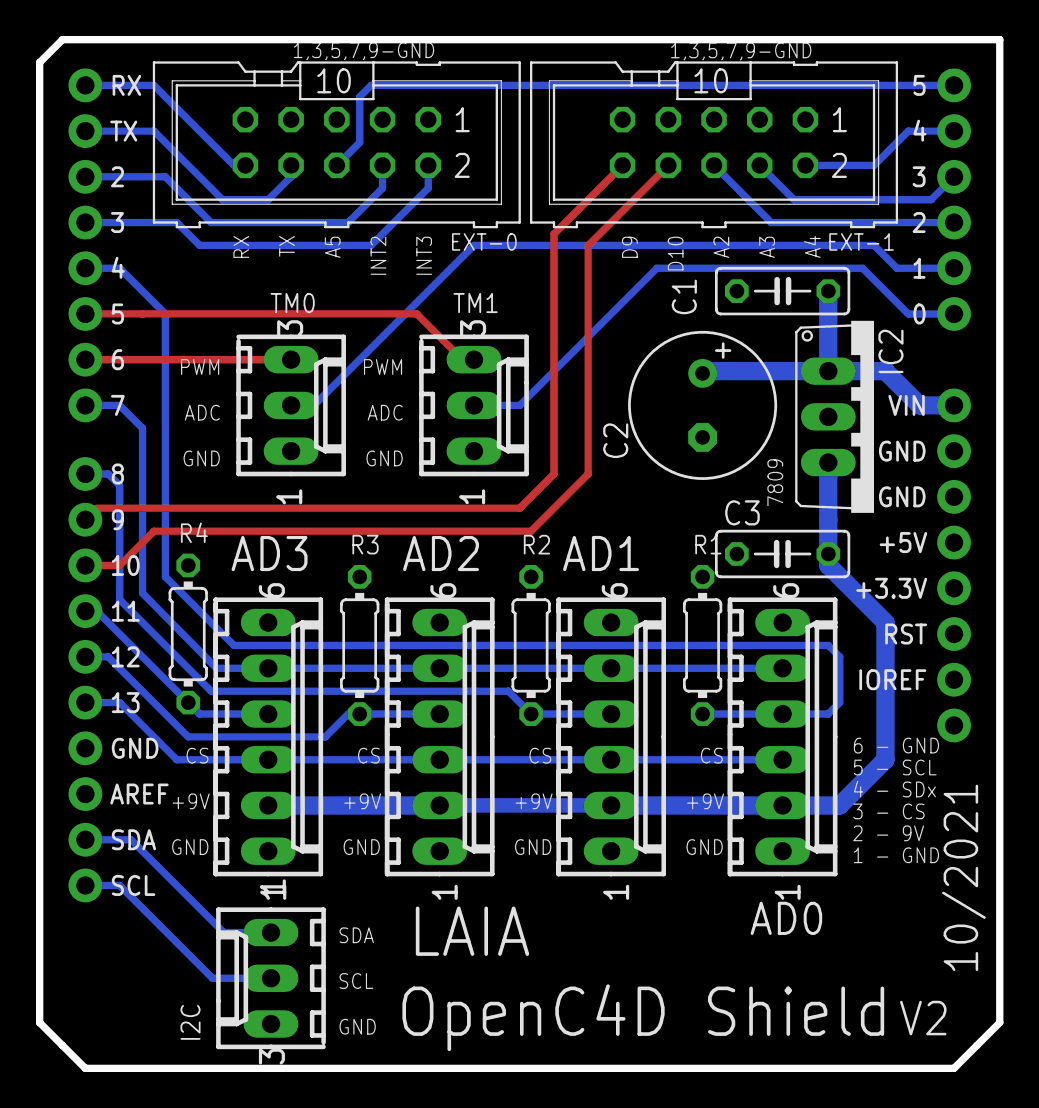
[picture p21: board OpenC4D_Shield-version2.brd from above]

Board: 2 copper layers, 53.3 x 57.1 mm, 18 parts (0 on the bottom side), 25 nets.

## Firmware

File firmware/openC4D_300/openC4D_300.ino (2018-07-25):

// Arduino Firmware for openC4D

#include "Arduino.h"
#include <Serine.h>

// Virtual devices living in this microcontroller
SerineVirtualDevice detectorVD = {'d', "SdL013002"};

// Definitions for this microcontroller
const byte INT_START = 2; // Interrupt (INT) to be used when CE starts the data acquisition
const byte PORT_START = 7; // This is the digital port that corresponds to the INT above.
const byte INT_STOP = 3; // Interrupt (INT) to be used when CE stops the data acquisition
const byte PORT_STOP = 8; // This is the digital port that corresponds to the INT above.
const byte LED = 11;
const byte SCK_AD = 20; // Serial Clock for the ADC MCP3551
const byte CS_AD = 16; // Chip Select for the ADC MCP3551
const byte SDO_AD[] = {// pins for all the ADCs
    18, 17, 19, 21
};

SerineChronometer mainChrono, ADCchrono, slowThingsChrono, connectionChrono;
boolean notConnected = true;
unsigned long timeOfConnection = 4294967295UL;
char sender = detectorVD.id; // At the beginning, the sender is the detector (We need one... not a big deal)
boolean continuousMode = false;
boolean waitForStart = false;
boolean waitForStop = false;
char separador = 'f';
boolean includeTime = true;
boolean incluiAD[] = {
    true, true, false, false
};

SerineBuffer usbChannel;

/**
 * The ADCs are continuously read, and the new values are posted in regData
 * structures. Every time the user ask for new ADC values, the most recent 
 * not-read values are sent back.
 */

struct regData {
    unsigned long time;
    unsigned long adc[4];
};

union regGet {
    regData adValue;
    byte stream[20];
};
regGet rGet[2] = {
    {
        0, 0, 0, 0, 0
    }
    ,
    {
        0, 0, 0, 0, 0
    }
};
byte toBeGet = 0;

void answerGetStatus() {
    if (separador == 'f') {
        Serial.print(sender);
        Serial.print(detectorVD.id);
        Serial.print("gS");
        Serial.print(continuousMode ? 'T' : 'F');
        Serial.print(waitForStart ? 'T' : 'F');
        Serial.print(waitForStop ? 'T' : 'F');
        Serial.print(';');
    }
}

void answerGet() {
    char answer[] = "0000000";
    if (separador == 'f') {
        Serial.print(sender);
        Serial.print(detectorVD.id);
        Serial.print('g');
        if (incluiAD[0] || incluiAD[1]) {
            Serial.print('A');
            usbChannel.putUL(rGet[toBeGet].adValue.time, 0, 6, answer);
            Serial.print(answer);
            usbChannel.putUL(rGet[toBeGet].adValue.adc[0], 0, 6, answer);
            Serial.print(answer);
            usbChannel.putUL(rGet[toBeGet].adValue.adc[1], 0, 6, answer);
            Serial.print(answer);
            Serial.print(';');
        };
        if (incluiAD[2] || incluiAD[3]) {
            Serial.print('B');
            usbChannel.putUL(rGet[toBeGet].adValue.time, 0, 6, answer);
            Serial.print(answer);
            usbChannel.putUL(rGet[toBeGet].adValue.adc[2], 0, 6, answer);
            Serial.print(answer);
            usbChannel.putUL(rGet[toBeGet].adValue.adc[3], 0, 6, answer);
            Serial.print(answer);
            Serial.print(';');
        };
    } else {
        if (includeTime) {
            usbChannel.putUL(rGet[toBeGet].adValue.time, 0, 6, answer);
            Serial.print(answer);
        }
        for (int i = 0; i < 4; i++)
            if (incluiAD[i]) {
                Serial.print(separador);
                usbChannel.putUL(rGet[toBeGet].adValue.adc[i], 0, 6, answer);
                Serial.print(answer);
            }
        Serial.println();
    }
}

void inline handleDetector(char *message) {
    switch (message[2]) {
        case 'G': // Get
            sender = message[1];
            switch (message[3]) {
                case 'r':
                    continuousMode = true;
                    waitForStart = false;
                    waitForStop = false;
                    answerGetStatus();
                    break;
                case 'w':
                    continuousMode = false;
                    waitForStart = true;
                    waitForStop = false;
                    answerGetStatus();
                    break;
                case 't':
                    continuousMode = false;
                    waitForStart = true;
                    waitForStop = true;
                    answerGetStatus();
                    break;
                case 'h':
                    continuousMode = false;
                    waitForStart = false;
                    waitForStop = false;
                    answerGetStatus();
                    break;
                case 'S':
                    answerGetStatus();
                    break;
                default: answerGet();
            };
            break;
        case 'S': // Set
            switch (message[3]) {
                case 't':
                    separador = '\t';
                    break;
                case 's':
                    separador = ' ';
                    break;
                default:
                    separador = message[3];
            }
            includeTime = (message[4] == '1');
            for (int i = 0; i < 4; i++)
                incluiAD[i] = (message[5 + i] == '1');

            break;
        case 'Z': // Zero
            mainChrono.zero();
            break;
        case 'X': // Connect
            connectionChrono.zero();
            notConnected = (message[3] == 'F');
            if (!notConnected) {
                if (message[4] != ';')
                    timeOfConnection = usbChannel.getUL(4, 7, message);
                else timeOfConnection = 4294967295UL;
            }
            if (notConnected) {
                continuousMode = false;
                waitForStart = false;
                waitForStop = false;
            }
            char answer[32];
            answer[0] = message[1];
            answer[1] = message[0];
            answer[2] = 'x';
            answer[3] = notConnected ? 'F' : 'N';
            answer[4] = ';';
            answer[5] = 0;
            Serial.print(answer);
            break;
        case 'I':
            if (message[3] == 'x') {
                serineChangeID(&detectorVD, message);
            } else {
                serineAnswerID(message[1], detectorVD, answer);
                Serial.print(answer);
            }
            serineAnswerID(message[1], detectorVD, answer);
            Serial.print(answer);
            break;
        default:
            serineIdontKnow(message, detectorVD.id, answer);
            Serial.print(answer);
    }
}

void inline handleBroadcast(char *message) {
    char answer[MAX_MESSAGE];
    switch (message[2]) {
        case 'I':
            serineAnswerID(message[1], detectorVD, answer);
            Serial.print(answer);
            break;
        default:
            serineIdontKnow(message, detectorVD.id, answer);
            Serial.print(answer);
    }
}

void started() {
    if (waitForStart) {
        delayMicroseconds(100);
        if (digitalRead(PORT_START) == LOW) { // check if this is a real start
            mainChrono.zero();
            continuousMode = true;
            waitForStart = false;
            answerGetStatus();
        }
    };
}

void stopped() {
    if (waitForStop) {
        delayMicroseconds(100);
        if (digitalRead(PORT_STOP) == LOW) { // check if this is a real stop
            continuousMode = false;
            waitForStart = false;
            waitForStop = false;
            answerGetStatus();
        }
    };
}

void setup() {
    Serial.begin(115200);
    pinMode(LED, OUTPUT);
    digitalWrite(LED, LOW);
    // Prepare for external start
    pinMode(PORT_START, INPUT_PULLUP);
    attachInterrupt(INT_START, started, FALLING);
    // Prepare for external stop
    pinMode(PORT_STOP, INPUT_PULLUP);
    attachInterrupt(INT_STOP, stopped, FALLING);
    // Prepare the ADCs
    for (int i = 0; i < 4; i++) digitalWrite(SDO_AD[i], LOW);
    for (int i = 0; i < 4; i++) pinMode(SDO_AD[i], INPUT);
    pinMode(SCK_AD, OUTPUT);
    digitalWrite(SCK_AD, LOW);
    pinMode(CS_AD, OUTPUT);
    digitalWrite(CS_AD, HIGH);
    delay(100);
    digitalWrite(CS_AD, LOW);
    // Prepare the timers
    mainChrono.zero();
    slowThingsChrono.zero();
    connectionChrono.zero();
}

void inline takeCareADC() {
    byte keepGoing = HIGH;
    byte numberOfTimes = 0;
    while (keepGoing == HIGH) {
        delay(1);
        keepGoing = LOW;
        for (int i = 0; i < 4; i++)
            keepGoing = keepGoing | digitalRead(SDO_AD[i]);
        numberOfTimes++;
        if (numberOfTimes > 100) keepGoing = false;
    };

    unsigned long timeADC = mainChrono.now();

    /**
     * Read the first three bits. The following patterns may happen:
     * 000 - 0 - OK
     * 001 - 1 - positive overflow
     * 010 - 2 - negative overflow
     */
    byte ovl[4];
    for (int i = 0; i < 4; i++) ovl[i] = 0;
    for (byte j = 0; j < 3; j++) {
        digitalWrite(SCK_AD, HIGH);
        delayMicroseconds(1);
        for (int i = 0; i < 4; i++) ovl[i] = (ovl[i] << 1) | digitalRead(SDO_AD[i]);
        digitalWrite(SCK_AD, LOW);
    }
    /* Reads the first bit and inverts it to produce positive numbers only*/
    unsigned long ad[4];
    digitalWrite(SCK_AD, HIGH);
    delayMicroseconds(1);
    for (int i = 0; i < 4; i++) ad[i] = (digitalRead(SDO_AD[i]) == HIGH) ? 0 : 1;
    digitalWrite(SCK_AD, LOW);
    /* Read the other bits*/
    for (byte j = 4; j < 25; j++) {
        digitalWrite(SCK_AD, HIGH);
        delayMicroseconds(1);
        for (int i = 0; i < 4; i++) ad[i] = (ad[i] << 1) | digitalRead(SDO_AD[i]);
        digitalWrite(SCK_AD, LOW);
    }
    /* Indicates overflow whether it happens. */
    for (int i = 0; i < 4; i++)
        if (ovl[i] == 1) ad[i] = 16777215UL;
        else if (ovl[i] == 2) ad[i] = 0;
    /**
     * Transfers the information to the register Get. This register has two 
     * positions: 0 and 1.
     */
    byte pos = 1 - toBeGet;
    rGet[pos].adValue.time = timeADC;
    for (int i = 0; i < 4; i++) rGet[pos].adValue.adc[i] = ad[i];
    toBeGet = pos; // point to these new ADC values
}

void loop() {
    /**
     * After each A/D conversion, there is room (~73 ms) for other activities
     * before the next A/D datum.
     */
    ADCchrono.zero();
    while (!ADCchrono.expired(55)) {
        // Take care of messages from USB
        while (Serial.available() && (usbChannel.getSpace() > 1)) usbChannel.putChar(Serial.read());
        char message[MAX_MESSAGE];
        usbChannel.getMessage(message);
        if (message[0] != 0) {
            if (message[0] == detectorVD.id) handleDetector(message);
            else if (message[0] == 'B') handleBroadcast(message);
        };
        // Executes all the timed procedures here (if some)
    };
    // Get new values from ADC 
    digitalWrite(LED, HIGH);
    takeCareADC();
    digitalWrite(LED, LOW);
    // Other tasks
    if (continuousMode) answerGet();
    if (slowThingsChrono.expired(800)) {
        slowThingsChrono.zero();
        if (connectionChrono.expired(timeOfConnection)) {
            notConnected = true;
            continuousMode = false;
        }
        if (notConnected) {
            Serial.print('B');
            Serial.print(detectorVD.id);
            Serial.print('i');
            Serial.print(detectorVD.serial);
            Serial.print(';');
        }
    }
}

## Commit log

2018-07-27 The hardware
    [board outline.gbr, bottom mask.gbr, bottom.gbr, drill.drl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]
2019-10-31 new C4D hardware
    [BoardOutline.gbr, BottomMask.gbr, BottomPaste.gbr, Through.drl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]
2021-10-28 firmware 4.0 and frontend 1.1
    new versions of firmware (now for Arduino UNO) and frontend (jSSC was uptaded)
2023-01-26 Teensy version was moved to a folder
    [CE-01-02-04_v01.brd, CE-01-02-04_v01.sch]
2023-01-26 Arduino version
    [OpenC4D_Shield-version2.brd, OpenC4D_Shield-version2.sch, copper_bottom.gbr, copper_top.gbr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]

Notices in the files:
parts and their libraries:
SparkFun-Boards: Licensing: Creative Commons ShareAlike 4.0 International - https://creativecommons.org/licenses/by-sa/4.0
